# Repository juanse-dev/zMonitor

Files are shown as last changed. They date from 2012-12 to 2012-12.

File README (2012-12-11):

zMonitor

Director:
- Fredy E. Segura Ph.D      (fsegura@uniandes.edu.co)

Autores:
- Juan Sebastian Cifuentes  (j-cifuen@uniandes.edu.co)
- Viviana Salcedo           (vp.salcedo93@uniandes.edu.co)

zMonitor es un dispositivo para la adquisición de señales de EEG y su visualización en Android desarrollado en el curso de Sistemas Embebidos de la Universidad de los Andes.

Se puede ver un video del funcionamiento de zMonitor en http://www.youtube.com/watch?v=pW1bedwvCxc

El proyecto se encuentra organizado por carpetas de la siguiente manera:
- Android: Archivos de la aplicación en Android.
- Microcontrolador: Programa en C para la adquisición de los datos y el envío por bluetooth.
- PCB-Eagle: Circuitos y PCBs en Eagle.
- README: Este archivo.

Características:
- Frecuencia de muestreo: 500Hz
- Resolución del ADC: 10bits
- Ganancia: Variable, de 1 a 100000*
- Banda pasante: 1 - 40Hz por medio de 2 filtros butterworth de 2 y 3 orden.
- Bluetooth baudrate: 57600bps
- Alimentación: Batería Lipo (3.7V)

* Amplificador por arreglar

ToDo:
- Arreglar Amplificador
- Guardar datos en archivo
- Enviar a base de datos
- Visualizador para la base de datos
- Mejorar trigger

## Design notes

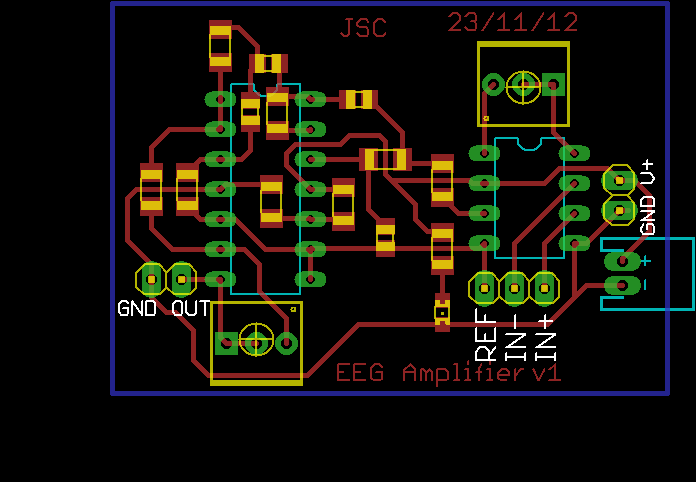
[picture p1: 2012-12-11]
PCB-Eagle/ADQ/TOP.png

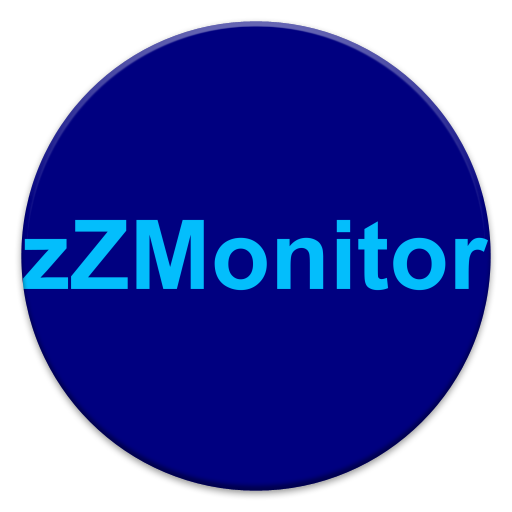
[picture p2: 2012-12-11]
Android/com.example.zzmonitor.ZMonitor/ic_launcher-web.png

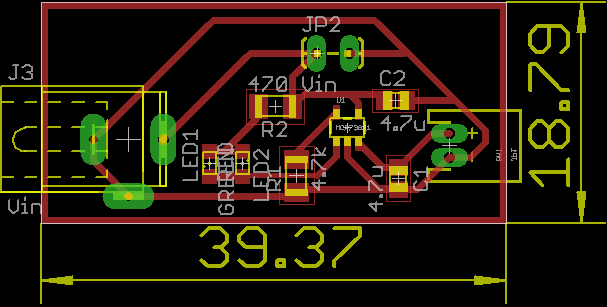
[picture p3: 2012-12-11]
PCB-Eagle/Lipo Charger/Lipo.bmp

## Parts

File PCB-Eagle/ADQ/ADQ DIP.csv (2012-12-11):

Qty | Value | Device | Package | Parts | Description | MF | MPN | OC_FARNELL | OC_NEWARK
1 |  | M02JST-PTH-2 | JST-2-PTH | JP1 | Header 2
1 | 100k | R-US_R1206 | R1206 | R4 | RESISTOR, American symbol
1 | 100k OHM | TRIMPOT | 3362U-2 | R6
1 | 100n | C-USC0805 | C0805 | C3 | CAPACITOR, American symbol
2 | 10u | C-USC0805 | C0805 | C2, C5 | CAPACITOR, American symbol
2 | 1k | R-US_R1206 | R1206 | R7, R13 | RESISTOR, American symbol
1 | 220n | C-USC0805 | C0805 | C1 | CAPACITOR, American symbol
1 | 22k | R-US_R1206 | R1206 | R14 | RESISTOR, American symbol
2 | 33k | R-US_R1206 | R1206 | R2, R3 | RESISTOR, American symbol
1 | 500 OHM | TRIMPOT | 3362U-2 | R1
3 | 51k | R-US_R1206 | R1206 | R5, R8, R9 | RESISTOR, American symbol
1 | AD620N | AD620N | DIL08 | IC1 | Low Cost, Low Power, Instrumentation Amplifier | ALTERA CORPORATION | AD620AN | 1523782 | 05F7108
1 | GREEN | LEDCHIPLED_0805 | CHIPLED_0805 | LED1 | LED
1 | INPUT | PINHD-1X3 | 1X03 | JP4 | PIN HEADER
1 | OUTPUT | PINHD-1X2 | 1X02 | JP2 | PIN HEADER
4 | STAND-OFF | STAND-OFF | STAND-OFF | JP3, JP6, JP7, JP8 | Stand Off
1 | TL074P | TL074P | DIL14 | IC2 | OP AMP
1 | V+ alt | PINHD-1X2 | 1X02 | JP5 | PIN HEADER

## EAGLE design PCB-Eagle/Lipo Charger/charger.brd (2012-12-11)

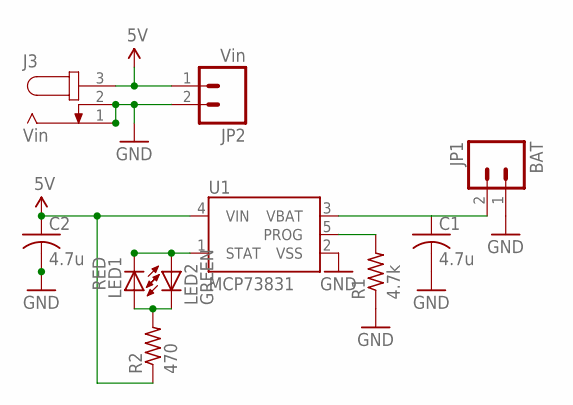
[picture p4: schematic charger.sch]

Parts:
C1, C2: 4.7u; C0805
J3: Vin; SPC4077
JP1: BAT; JST-2-PTH
JP2: Vin; 1X02_LOCK_LONGPADS
LED1: RED; SML0805
LED2: GREEN; SML0805
R1: 4.7k; M1206
R2: 470; M1206
U1: MCP73831; SOT23-5

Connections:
5V: C2.1, J3.3, JP2.1, R2.1, U1.4 (VIN)
GND: C1.2, C2.2, J3.1, J3.2, JP1.1, JP2.2, R1.1, U1.2 (VSS)
unnamed: LED1.A, LED2.C, R2.2
unnamed: LED1.C, LED2.A, U1.1 (STAT)
unnamed: R1.2, U1.5 (PROG)
unnamed: C1.1, JP1.2, U1.3 (VBAT)

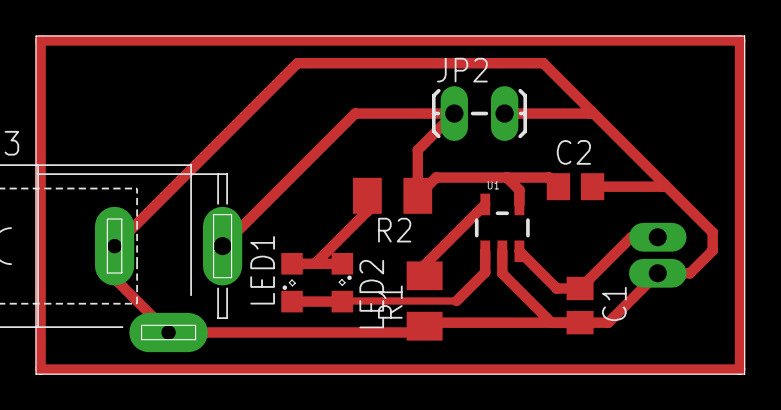
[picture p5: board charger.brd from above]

Board: 2 copper layers, 39.4 x 18.8 mm, 10 parts (1 on the bottom side), 6 nets.

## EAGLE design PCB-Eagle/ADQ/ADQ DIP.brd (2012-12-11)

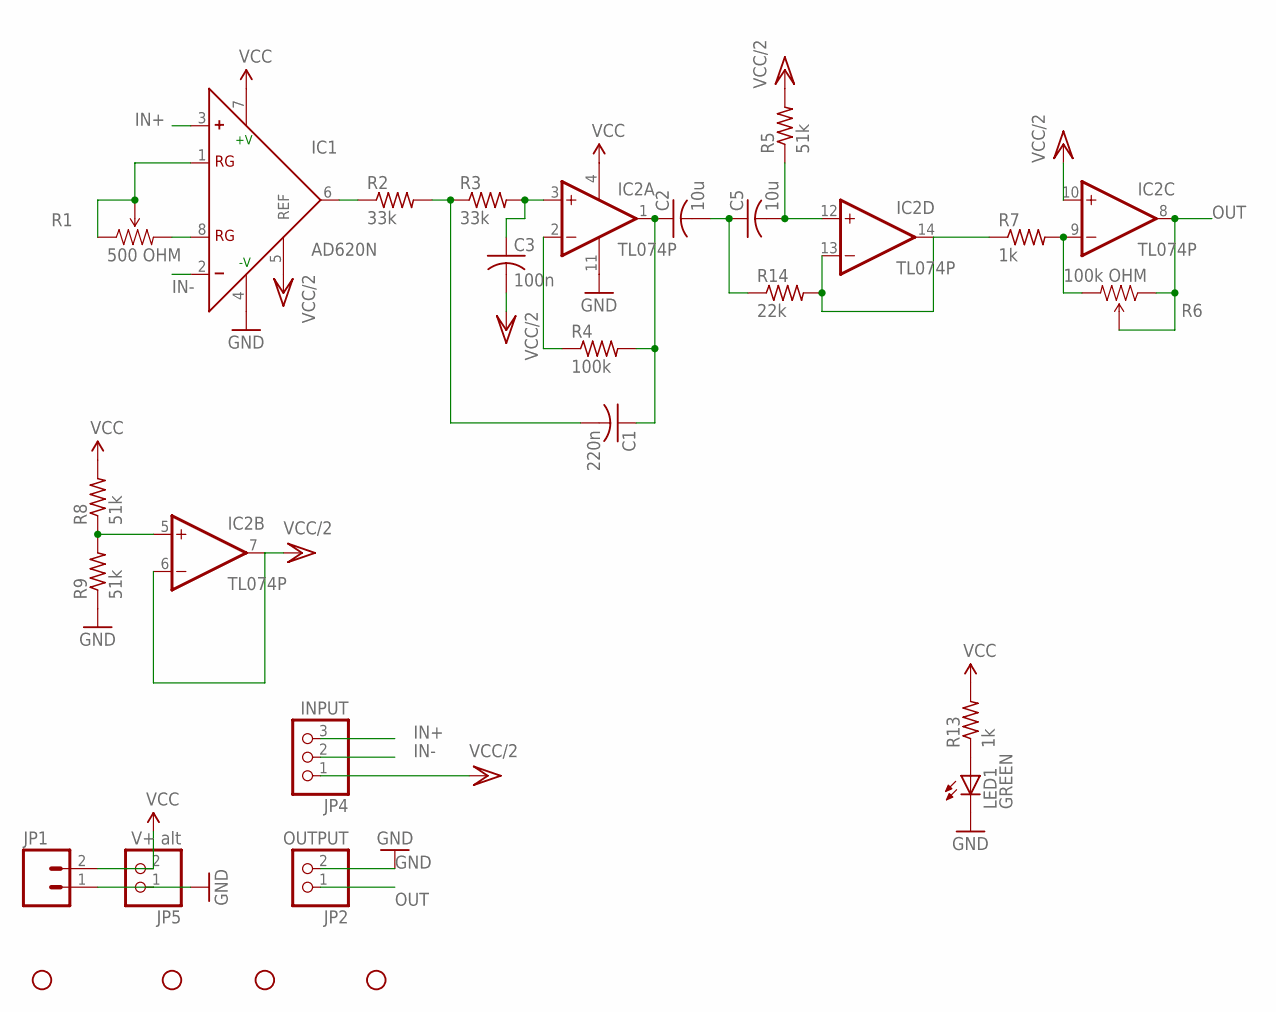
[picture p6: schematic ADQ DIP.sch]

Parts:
C1: 220n; C0805
C2, C5: 10u; C0805
C3: 100n; C0805
IC1: AD620N; DIL08; MPN AD620AN
IC2: TL074P; DIL14
JP1: M02JST-PTH-2; JST-2-PTH
JP2: OUTPUT; 1X02
JP3, JP6, JP7, JP8: STAND-OFF
JP4: INPUT; 1X03
JP5: V+ alt; 1X02
LED1: GREEN; CHIPLED_0805
R1: 500 OHM; 3362U-2
R2, R3: 33k; R1206
R4: 100k; R1206
R5, R8, R9: 51k; R1206
R6: 100k OHM; 3362U-2
R7, R13: 1k; R1206
R14: 22k; R1206

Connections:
GND: IC1.4 (-V), IC2.11 (V-), JP1.1, JP2.2, JP5.1, LED1.C, R9.1
IN+: IC1.3 (+), JP4.3
IN-: IC1.2 (-), JP4.2
unnamed: IC1.8 (RG), R1.3 (CW)
unnamed: IC1.1 (RG), R1.1 (CCW), R1.2 (WIPER)
unnamed: C1.2, R2.2, R3.1
unnamed: IC1.6 (OUT), R2.1
unnamed: C3.1, IC2.3 (+IN), R3.2
unnamed: IC2.2 (-IN), R4.1
unnamed: C1.1, C2.1, IC2.1 (OUT), R4.2
unnamed: LED1.A, R13.1
unnamed: C2.2, C5.1, R14.1
unnamed: IC2.13 (-IN), IC2.14 (OUT), R7.1, R14.2
unnamed: IC2.5 (+IN), R8.1, R9.2
unnamed: IC2.9 (-IN), R6.3 (CW), R7.2
unnamed: C5.2, IC2.12 (+IN), R5.1
OUT: IC2.8 (OUT), JP2.1, R6.1 (CCW), R6.2 (WIPER)
VCC: IC1.7 (+V), IC2.4 (V+), JP1.2, JP5.2, R8.2, R13.2
VCC/2: C3.2, IC1.5 (REF), IC2.6 (-IN), IC2.7 (OUT), IC2.10 (+IN), JP4.1, R5.2

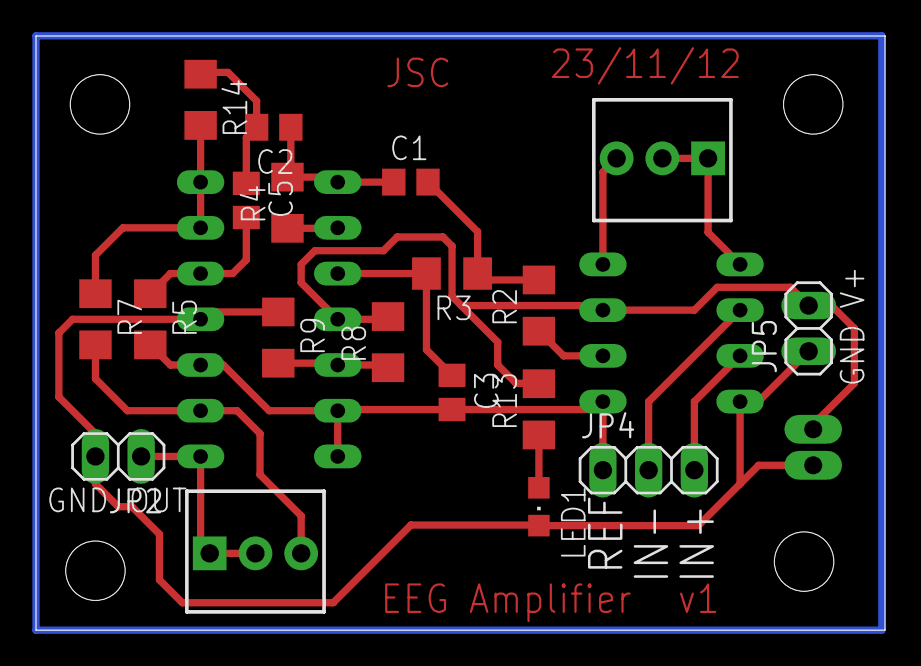
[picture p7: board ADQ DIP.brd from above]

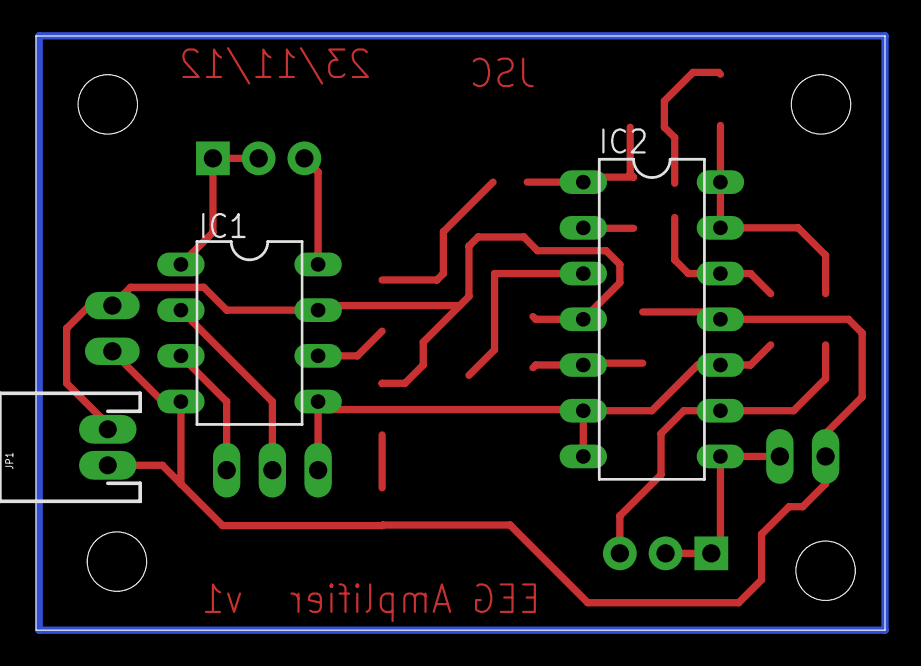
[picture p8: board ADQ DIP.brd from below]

Board: 2 copper layers, 47.2 x 33.0 mm, 26 parts (3 on the bottom side), 19 nets.

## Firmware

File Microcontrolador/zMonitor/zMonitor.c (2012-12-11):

#include <avr/io.h>
#define F_CPU 1000000UL  // 1 MHz
#include <stdio.h>
#include <stdlib.h>
#include <util/delay.h>
#include <avr/interrupt.h>
#include <avr/signal.h>
#include <inttypes.h>

//CONSTANTES PARA LA USART
//#define F_CPU 1000000UL  // 1 MHz
#define FOSC 157000//// Clock Speed
#define BAUD 9600
#define MYUBRR (FOSC/(8*BAUD))-1

// Constante de canal ADC a leer
#define CHANNEL 0

//Constante de tiempo de espera máximo para medida del cátodo (primera técnica)
#define MAX_DELAY 200

// Declaración de funciones
void USART_Init(unsigned int baud);
void USART_Transmit(unsigned char data);
unsigned char USART_Receive( void );
void ADC_init(void);
unsigned int ADC_read(unsigned char);
void enviarDatos(unsigned int sector);
unsigned char x= 0x00;
int contador=0;

int main(void){
	DDRB=0xFF;
	DDRD=0x03;
	USART_Init( MYUBRR );
	ADC_init();
	sei();
	unsigned int value;
	
	for(;;)
	{
		
		if(x==0xFF){
			value=ADC_read(CHANNEL);//Mide el canal definido por la constante
			enviarDatos(value);
			_delay_ms(200);
		}
		PORTB=x;
		
	}
}
void ADC_init(void) // Initialization of ADC
{
	ADMUX|=(1<<REFS0); // AVcc with external capacitor at AREF
	ADCSRA|=(1<<ADEN)|(1<<ADPS2)|(1<<ADPS1)|(1<<ADPS0);
	// Enable ADC and set Prescaler division factor as 128 (the fastest)
}

unsigned int ADC_read(unsigned char ch)
{
	ch= ch & 0b00000111; // channel must be b/w 0 to 7
	DDRC&=~(1<<ch);//Habilito el canal como entrada
	//PORTC|=(1<<ch); //Aseguro pull-up, es necesario?
	ADMUX |= ch; // selecting channel
	
	ADCSRA|=(1<<ADSC); // start conversion
	while(!(ADCSRA & (1<<ADIF))); // waiting for ADIF, conversion complete
	ADCSRA|=(1<<ADIF); // clearing of ADIF, it is done by writing 1 to it
	
	return (ADC);
}


void USART_Init( unsigned int baud )
{
	/* Set baud rate */
	UBRRH |= (unsigned char)(baud>>8);
	UBRRL |= (unsigned char)baud;
	/* Enable  transmitter */
	UCSRB |= (1<<TXEN)|(1<<RXEN)|(1<<RXCIE);
	/* Set frame format: 8data, 1stop bit */
	UCSRC |= (1<<URSEL)|(3<<UCSZ0);
	UCSRA|=(1<<U2X);
	sei();
}

void USART_Transmit( unsigned char data )
{
	/* Wait for empty transmit buffer */
	while ( !( UCSRA & (1<<UDRE)) )
	;
	/* Put data into buffer, sends the data */
	UDR = data;
}

unsigned int USART_Check( void )
{
	int recibio=0;
	/* Wait for data to be received */
	if( (UCSRA & (1<<RXC)) )
	{
		recibio=1;
	}

	/* Get and return received data from buffer */
	return recibio;
}

unsigned char USART_Receive( void )
{
	/* Wait for data to be received */
	while ( !(UCSRA & (1<<RXC)) )
	;
	/* Get and return received data from buffer */
	return UDR;
}


void enviarDatos(unsigned int sector){
	char mensaje[20];
	sprintf( mensaje, "(%d,%d)", contador, sector );
	for(int i=0;i<sizeof(mensaje);i++){
		unsigned char dato= mensaje[i];
		USART_Transmit( dato );
		if(dato==0x29)break;
		_delay_ms(200);
	}	
	contador++;
}


SIGNAL (SIG_UART_RECV) { // USART RX interrupt
	unsigned char h= USART_Receive();
	if( h ==0x4F )
	{
		h= USART_Receive();
		if(h==0x4B)
		{
			x=0xFF;
		}
	}
	else if(h==0x45)
	{
		h= USART_Receive();
		if(h==0x4E)
		{
			h= USART_Receive();
			if(h==0x44)
			{
				contador=0;
				x=0x00;
			}
		}
	}
}

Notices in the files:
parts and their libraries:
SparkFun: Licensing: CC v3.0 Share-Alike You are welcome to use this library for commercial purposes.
